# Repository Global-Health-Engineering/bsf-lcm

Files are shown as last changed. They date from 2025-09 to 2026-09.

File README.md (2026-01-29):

<!-- badges: start -->



<!-- badges: end -->

<h1> Black Soldier Fly Larvae Counting Machine </h1>

<b>Contributors</b>  
- Jonas Biner <a href="https://orcid.org/0009-0008-2161-3013">
ORCID logo 0009-0008-2161-3013
</a> *author, developer*  
- Jakub Tkaczuk <a href="https://orcid.org/0000-0001-7997-9423">
ORCID logo 0000-0001-7997-9423
</a> *supervisor, maintainer*  
- Christian Zurbrügg <a href="https://orcid.org/0000-0003-4980-4483">
ORCID logo 0000-0003-4980-4483
</a> *supervisor*  
- Stefan Diener <a href="https://orcid.org/0000-0002-6622-6980">
ORCID logo 0000-0002-6622-6980
</a> *supervisor*  
- Elizabeth Tilley <a href="https://orcid.org/0000-0002-2095-9724">
ORCID logo 0000-0002-2095-9724
</a> *supervisor*  

<br>
<p align="middle"> 

<br><br>
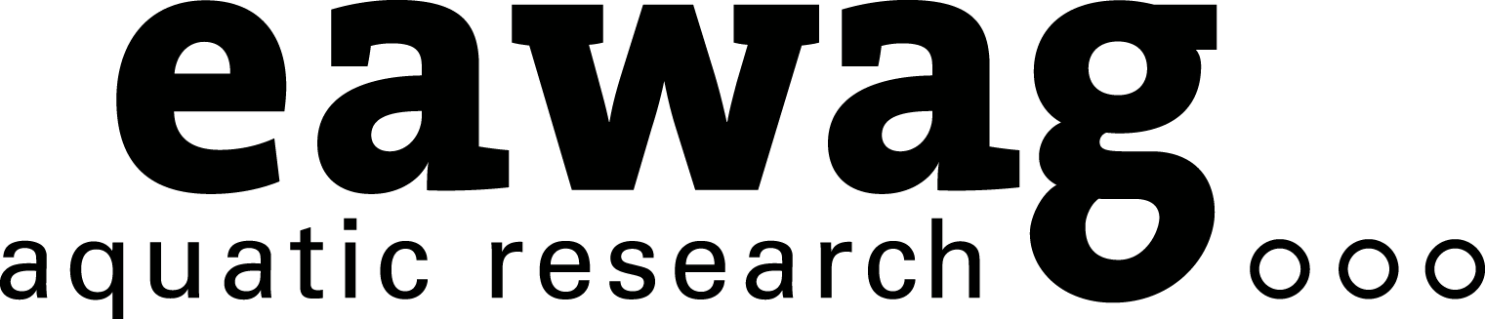
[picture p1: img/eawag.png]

<br><br>
<b>Complete description of system design, functionalities, and operation is available on  
<a href="https://global-health-engineering.github.io/bsf-lcm/">Github pages</a>  
</b>  
It compliments the openly-accessible master's thesis, available on the  
<a href="">ETH Research Collection</a>
</p>

# Overview

# Licenses

The three core elements of this project are licensed under:

| Component      | License                                                                                                |
|----------------|--------------------------------------------------------------------------------------------------------|
| Hardware       | [CERN-OHL-S 2.0](https://opensource.org/license/cern-ohl-s)                                            |
| Software       | [MIT](https://opensource.org/licenses/MIT)                                                             |
| Documentation  | [Creative Commons Attribution 4.0 International](https://creativecommons.org/licenses/by/4.0/)         |

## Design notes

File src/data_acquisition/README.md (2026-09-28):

# data-acquisition

'BSF_LCM_MK2.desktop' needs to be copied to '~/.config/autostart/' on Raspberry Pi for the program to start on boot.

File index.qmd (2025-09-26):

---
title: "Black Soldier Fly Larvae Counting Machine"
subtitle: "Design, Assembly, and Usage Manual"
number-sections: true
format: html
---

<!-- badges: start -->



<!-- badges: end -->

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

<br>
<p align="middle">
  
<br>
  
<br>
Github repository for this page sits [here](https://github.com/Global-Health-Engineering/bsf-lcm).
</p>

# Introduction {#sec-intro}

The Larvae Counting Machine (LCM) MK1 is designed to facilitate the counting of Five-Days-Old (5-DOL) Black Soldier Fly (BSF) larvae. It separates the larvae from frass and chicken feed to guarantee high homogeneity of the larvae batch making the sample more representative; and automates counting of samples. The process involves three steps:

- Sieving
- Sedimentation
- Counting

# Overview {#sec-overview}

The LCM MK1 consists of two funnels mounted on two flat boards and a 3D printed box containing the electronics. During operation the setup should look as shown in Figure 1.

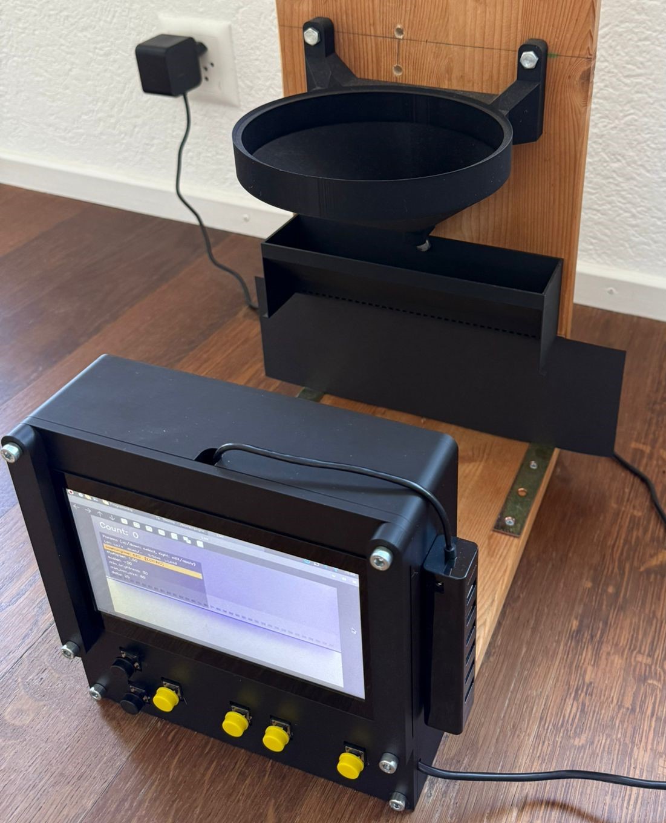
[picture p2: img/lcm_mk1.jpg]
Figure 1. Larvae Counting Machine Mark 1


The purpose of the first circular funnel is to facilitate the loading of larvae into the second funnel, which in turn forces them to spread out horizontally along the back wall and makes them fall out through holes on the side the funnel one after another. The falling larvae are filmed by a camera located at the back wall of the 3D printed electronics box. Then the LCM MK1 python program, running on a Raspberry Pi 5, uses frame differencing to count the larvae falling through the camera's field of view.

# Cost breakdown {#sec-costs}

# Licenses {#sec-license}

The three core elements of this project are licensed under:

| Component      | License                                                                                                |
|----------------|--------------------------------------------------------------------------------------------------------|
| Hardware       | [CERN-OHL-S 2.0](https://opensource.org/license/cern-ohl-s)                                            |
| Software       | [Apache 2.0](https://opensource.org/license/apache-2-0)                                                |
| Documentation  | [Creative Commons Attribution 4.0 International](https://creativecommons.org/licenses/by/4.0/)         |

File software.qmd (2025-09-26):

---
title: "Software"
number-sections: true
format: html
---

<!-- badges: start -->


<!-- badges: end -->

# Start up

To turn the larvae counting software on the Raspberry Pi 5:

- Plug in the power supply
- Wait until the Rapsberry Pi boots up
- Press and hold the **LCM Launch** icon, located on desktop
- Click **Open**
- Click **Execute**
- Double-click on the Top bar of the newly opened window to open it in a full screen mode

# Button Layout

The software allows the user to navigate the menu of the program with 6 built-in buttons. The function of each button is described in Figure 1.

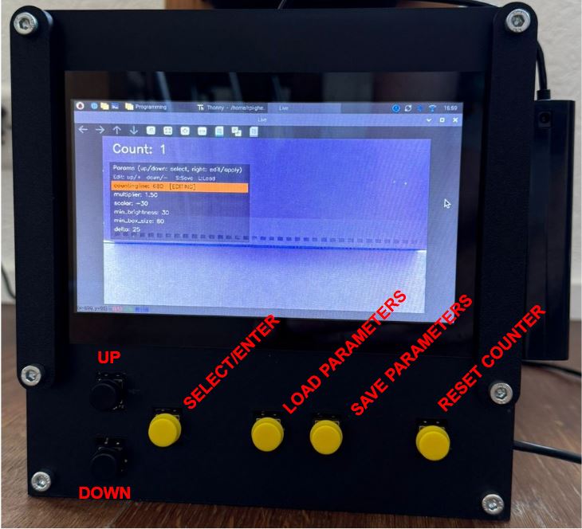
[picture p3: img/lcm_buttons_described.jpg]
Figure 1. Functional buttons


# Parameter Tuning

The constant parameters used by the software to differentiate and count the larvae can be tuned to adjust the system to the existing lighting conditions.

**Important**: All the images are converted into grey scale so each pixel has associated a single value ranging from 0 (black) to 255 (white).

The parameters used are as follows:

- **Multiplier** multiplies each pixel value of the taken images by a fixed value. It increases the contrast of the image but if the multiplied pixel value is 255 or higher, all pixes will be displayed as white.
- **Scalar**. This fixed number is added to each pixel value of the image so the the brightness of the black and white image can be changed.
- **Minimum brightness**. After the previous two transformations are applied to all pixes, the image is converted into a binary. Each pixel with value equal or higher than the minimum brightness is set to 255 (white) and all others are set to 0 (black).
- **Minimum box size** determines what minimum size in pixels a counted object, falling in front of the camera, should have. This parameter prevents counting of noise and chicken feed falling out of the funnel.
- **Delta** is used to prevent double counting of the same larvae by comparing the x coordinate of a larvae with the ones of previously counted larvae plus and minus the chosen delta value. Should a larvae have already been counted in the zone, the new box is not counted.
- **Counting line height**. In order to prevent the larvae from being counted while crawling around in the funnel, the program only counts the larvae below the counting line displayed in the live feed on the screen . The value should be set such that the line is always located right below the funnel, as shown in Figure 1.

The parameters should be set by default to make the machine operate according to expectations, so that only the **counting line height** should be adapted, if necessary. If frass particles smaller than the larvae are counted try increasing the **minimum box size**. If too many larvae are missed try decreasing the **minimum box size**.

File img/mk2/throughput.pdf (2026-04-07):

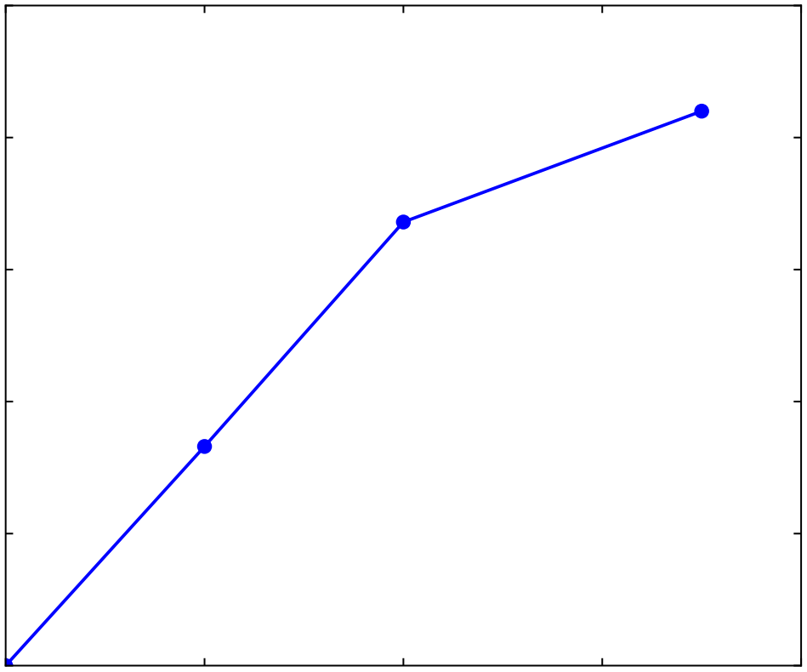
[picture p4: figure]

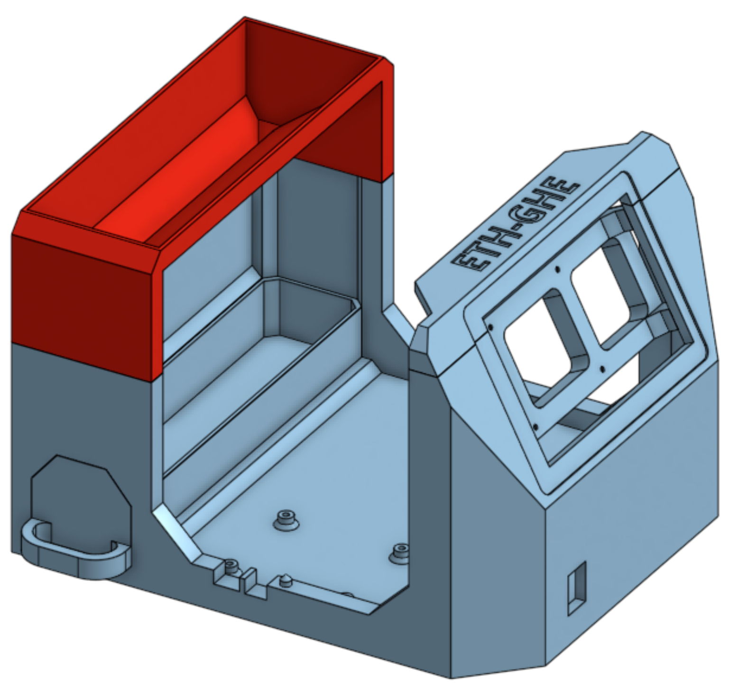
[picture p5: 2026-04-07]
img/mk2/divider_on_foundation_drawing.png

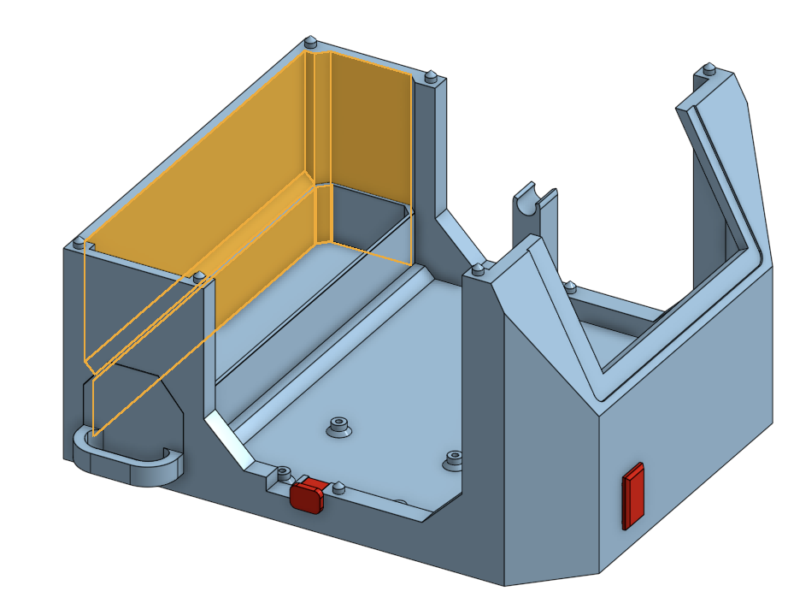
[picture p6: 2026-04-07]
img/mk2/painted_surface_right_view_drawing.png

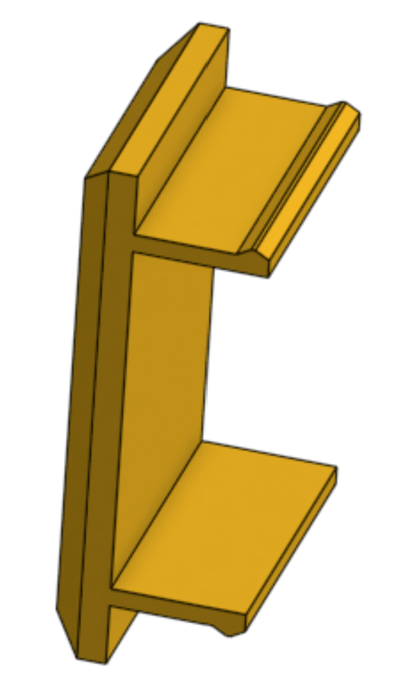
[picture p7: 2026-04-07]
img/mk2/cap_front_drawing.png

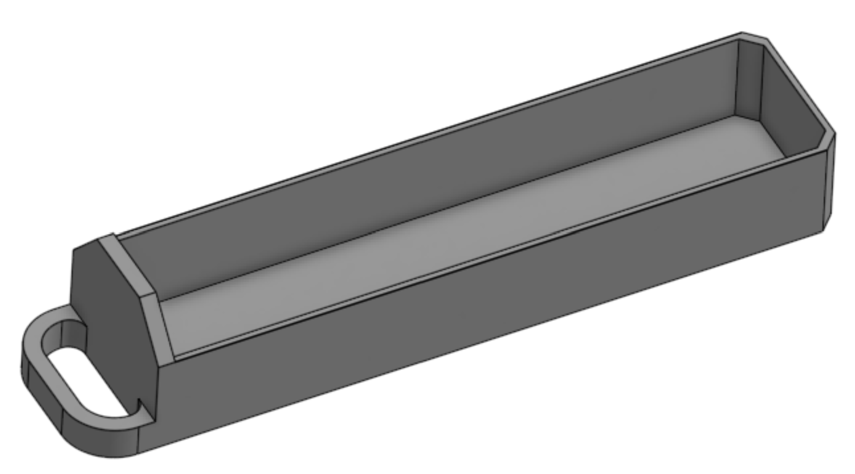
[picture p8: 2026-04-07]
img/mk2/collection_box_drawing.png

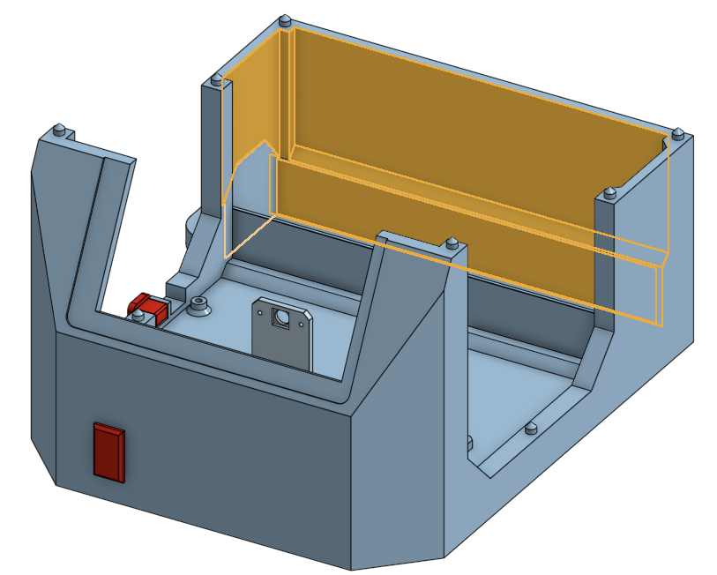
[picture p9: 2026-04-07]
img/mk2/painted_surface_left_view_drawing.png

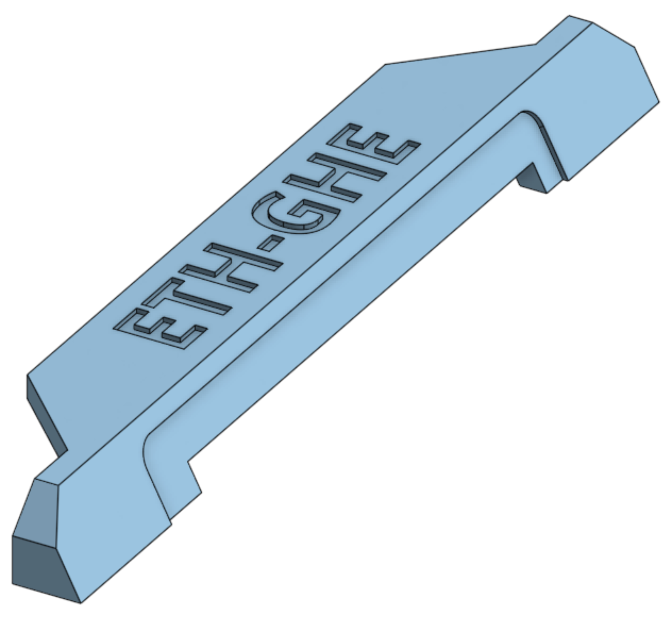
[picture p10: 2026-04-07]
img/mk2/top_part_drawing.png

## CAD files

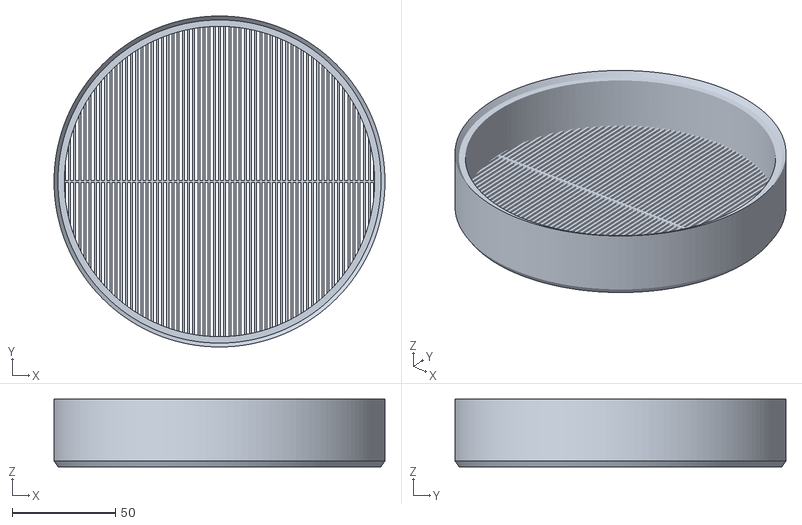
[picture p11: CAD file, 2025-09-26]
cad/mk1/150mm_sieve_1.5mm_1mm.stl
160.0 x 160.0 x 32.7

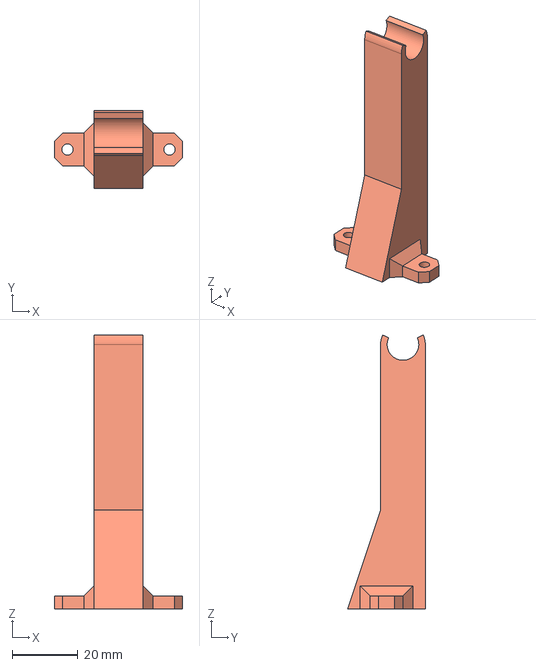
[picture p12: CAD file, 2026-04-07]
cad/mk2/counting/light_clamp.step
39.0 x 23.6 x 83.2 mm

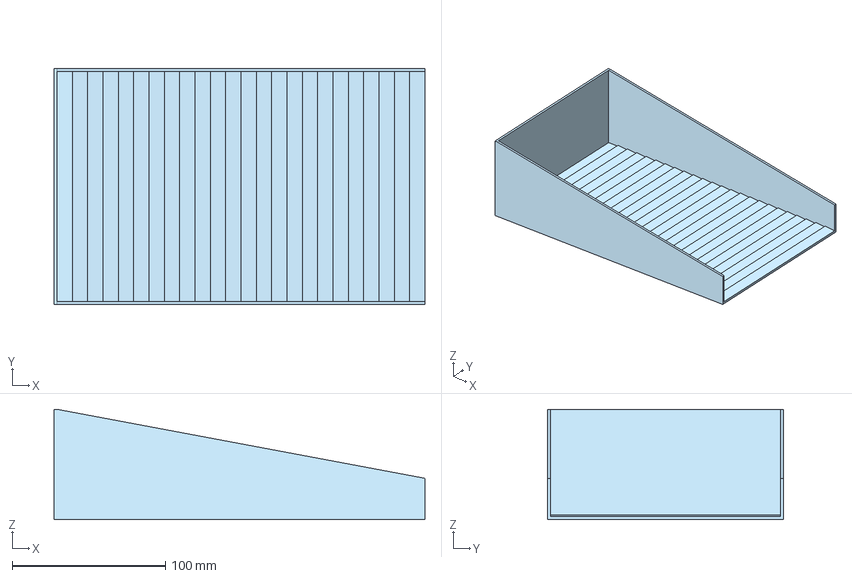
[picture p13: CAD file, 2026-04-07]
cad/mk2/separation/riffle_tray.step
242.0 x 154.0 x 72.0 mm

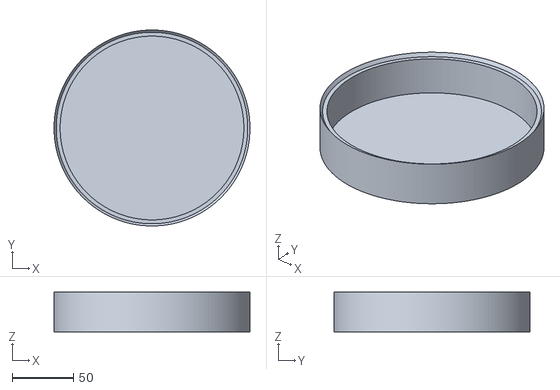
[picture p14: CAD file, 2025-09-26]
cad/mk1/150mm_collection_bowl.stl
160.0 x 160.0 x 32.6

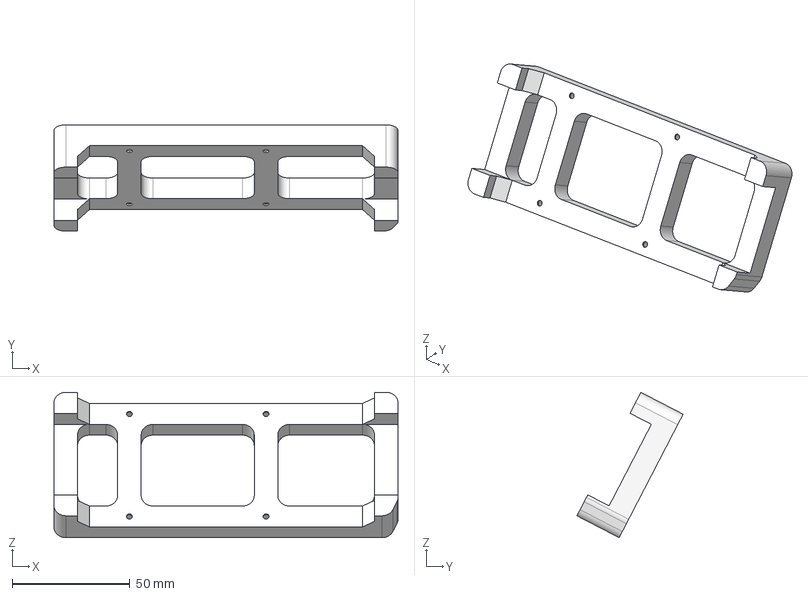
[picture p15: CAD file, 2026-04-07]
cad/mk2/counting/screen_clamp.step
146.0 x 45.1 x 61.7 mm

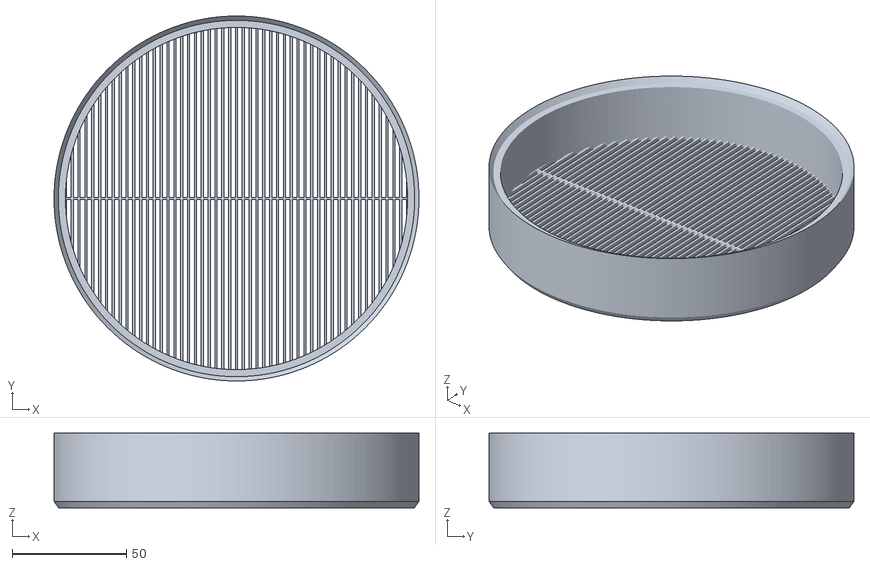
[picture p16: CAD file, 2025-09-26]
cad/mk2/separation/sieve_2mm_1mm.stl
160.0 x 160.0 x 32.7

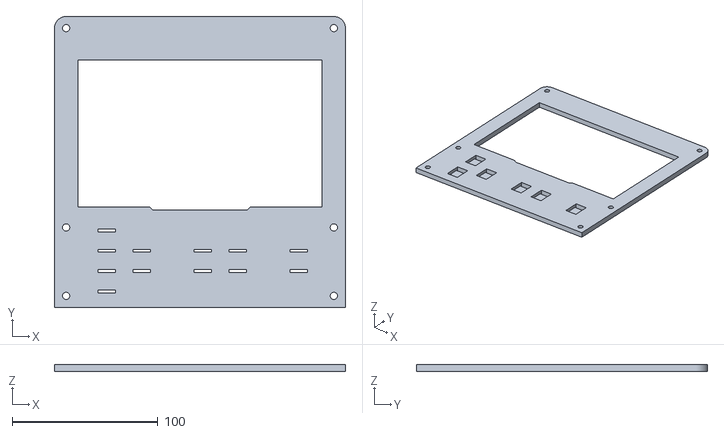
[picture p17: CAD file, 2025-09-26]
cad/mk1/lcm_front_plate.stl
200.0 x 200.0 x 5.00

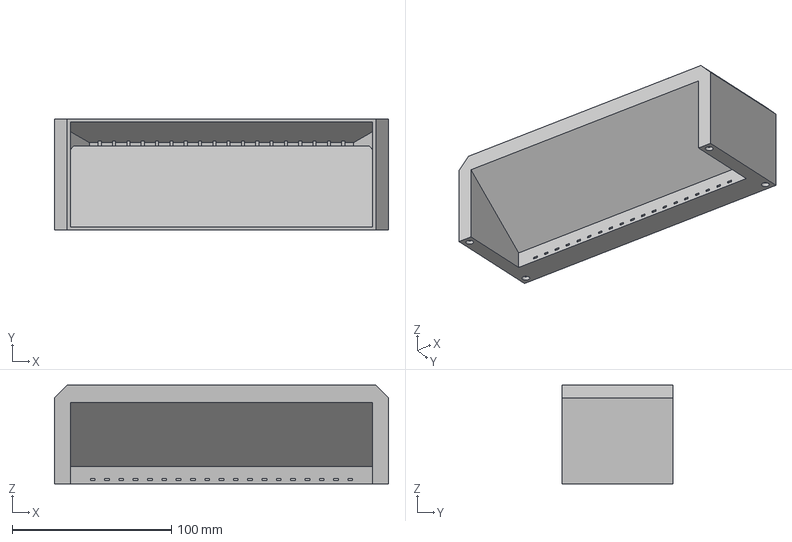
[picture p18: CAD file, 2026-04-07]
cad/mk2/counting/divider.step
210.0 x 70.0 x 62.0 mm

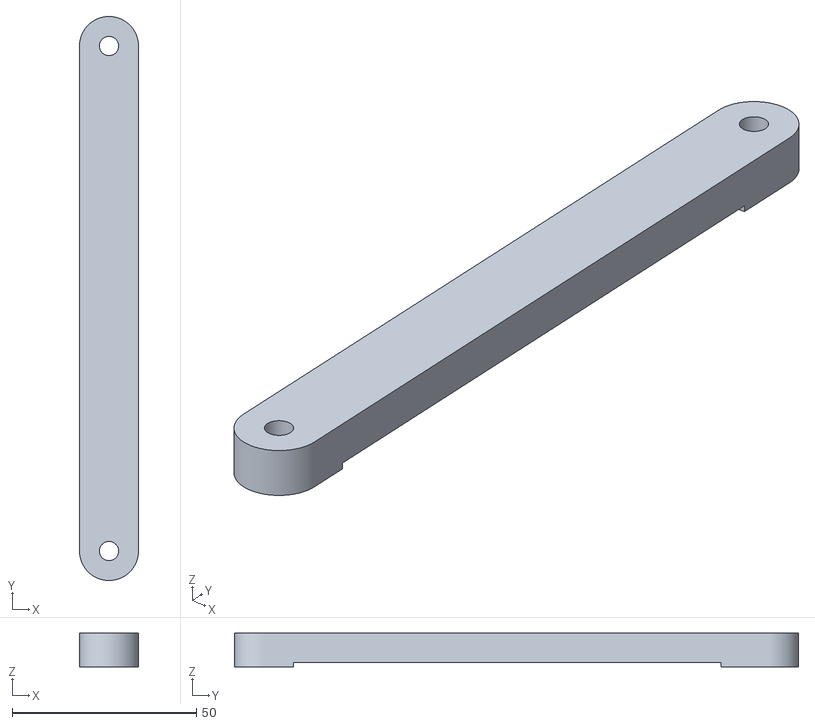
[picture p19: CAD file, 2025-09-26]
cad/mk1/lcm_screen_clamp.stl
16.0 x 153.0 x 9.20

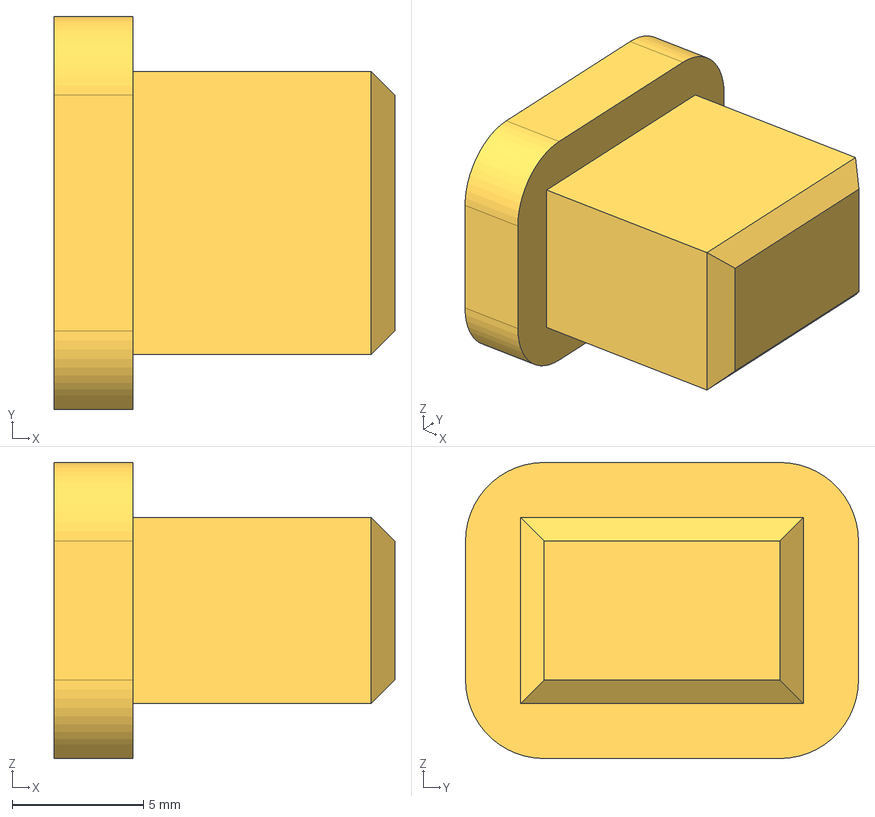
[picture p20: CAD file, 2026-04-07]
cad/mk2/counting/cap_left.step
13.0 x 15.0 x 11.3 mm

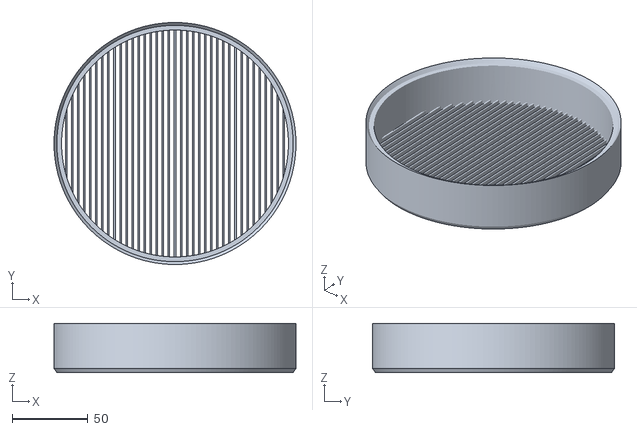
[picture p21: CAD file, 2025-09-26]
cad/mk1/150mm_sieve_3mm_1mm.stl
160.0 x 160.0 x 32.7

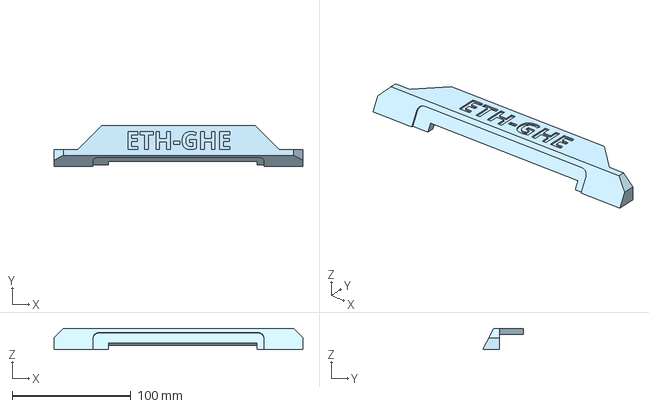
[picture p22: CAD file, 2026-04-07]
cad/mk2/counting/top_part.step
210.0 x 34.3 x 18.0 mm

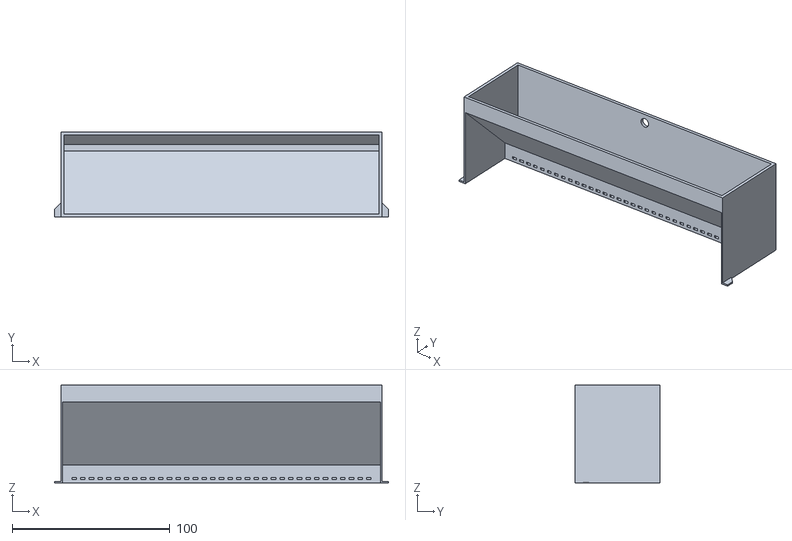
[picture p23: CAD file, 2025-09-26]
cad/mk1/collection_funnel_3x1.5mm.stl
212.0 x 54.0 x 62.0

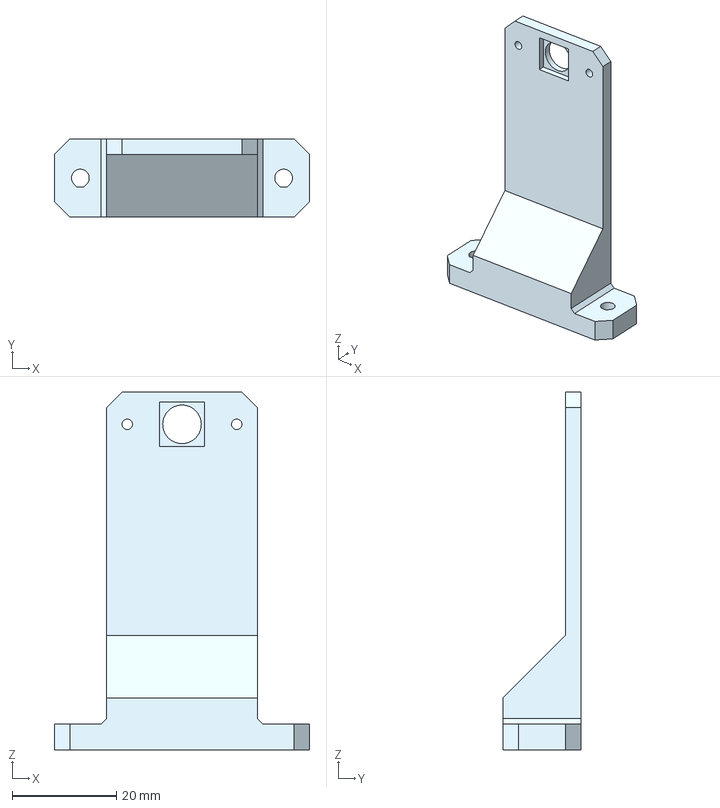
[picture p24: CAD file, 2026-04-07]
cad/mk2/counting/camera_mount.step
49.0 x 15.0 x 68.7 mm

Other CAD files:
cad/mk1/collection_box.stl
cad/mk1/150mm_funnel.stl
cad/mk1/lcm_box.stl
cad/mk1/lcm_cam_holder.stl
cad/mk2/counting/cap_front.step
cad/mk2/counting/collection_box.step
cad/mk2/counting/cover.step
cad/mk2/counting/foundation.step

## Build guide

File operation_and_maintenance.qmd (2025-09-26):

---
title: "Usage Manual"
number-sections: true
format: html
---

<!-- badges: start -->


<!-- badges: end -->

# Operation

Below, the the process of preparing and counting the 5-DOL with LCM MK1 is described. The entire batch of 5-DOL larvae should go through the sieving and the sedimentation step. This removes most of the chicken feed and frass from the larvae and removes larvae which are too small to be transferred and counted.

## Sieving

### Materials needed

- Sieves (3 mm, 2 mm, and 1.5 mm spacing)
- Collection bowl
- Two more containers (one for the larvae and one for the chicken feed)

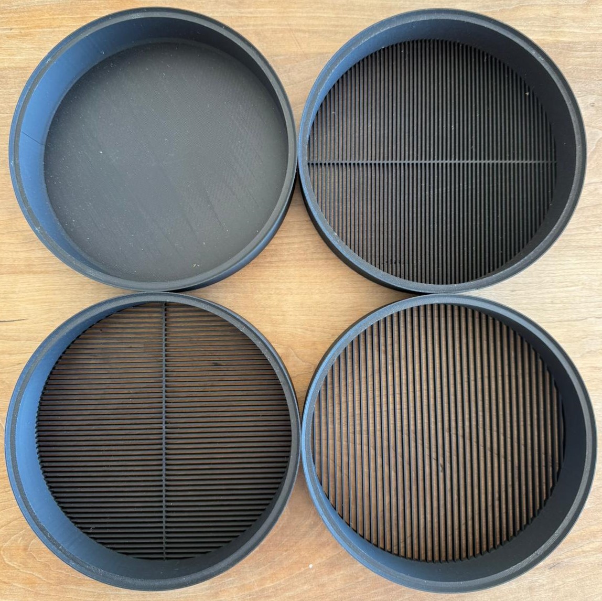
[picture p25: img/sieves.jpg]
Figure 1. Sieves


### Preparation

1. Place the collection bowl on the table.
2. Stack sieves on the bowl starting with the smallest gap on the bottom, progressing up to largest gap. Rotate each sieve 90° relative to sieve below. *(Only use 1.5 mm sieve if larvae are small enough to pass through it, otherwise they will get stuck).*

### Procedure

1. Pour **100 g of larvae mix** into the top sieve.
2. Remove the sieves one after another as soon as no more movement is spotted in the sieve (remove them carefully causing as little vibration as possible).
3. Pour the separated chicken feed from the removed sieves into chicken feed collection container.

Repeat the process if there are still large chunks of chicken feed visible in the larvae mix (2–3 times bigger than the size of the larvae).

**Important: Only process 100 g of larvae chicken feed mix per batch.**

## Sedimentation

The goal of the sedimentation step is to remove the frass from the previously sieved larvae. Additionally, by using the gold pan, larvae smaller than ~1 mm are also separated. To guarantee a high enough separation quality this step needs to be repeated multiple times.

### Materials needed

- Gold Pan  
- Container with sieved larvae (from the previous step)  
- 2 more containers (1 for processed larvae, 1 for frass to be dumped in)  

### Procedure

1. Hold the gold pan at an upward angle of around 45° and fill move the preprocessed larvae from the previous step into the gold pan (Processing 100 g of larvae and frass mix was successful; the maximum possible load must be found by trial and error), see Figure 2a.
2. Tilt the gold pan forward until larvae start pouring out into the collection container. Increase the angle steadily until all large larvae have fallen out of the pan, see Figures 2b and 2c.
3. Rotate the the gold pan back upwards to a steep angle and knock it on the back so the frass collects at the back side. Then knock from the side to move the frass into a corner. Pour the separated frass into the frass collection container *(Smaller larvae may remain in the frass and should be added back into the chicken feed larvae boxes for transfer and counting on a later day).*  

Repeat this three-step process until the amount of frass removed in each cycle decreases drastically. After finishing, pour the completely preprocessed larvae into another large collection container.  

::::{.columns}
::: {.column width="50%"}
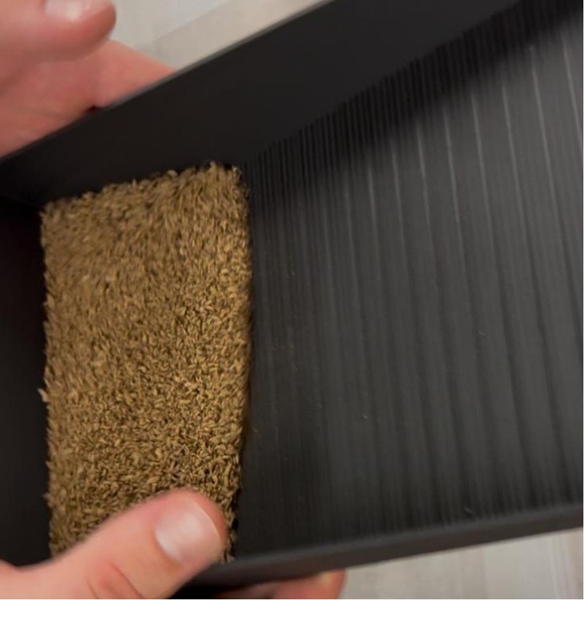
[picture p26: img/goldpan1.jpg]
Figure 2a. Fill the pan with larvae

:::

::: {.column width="50%"}
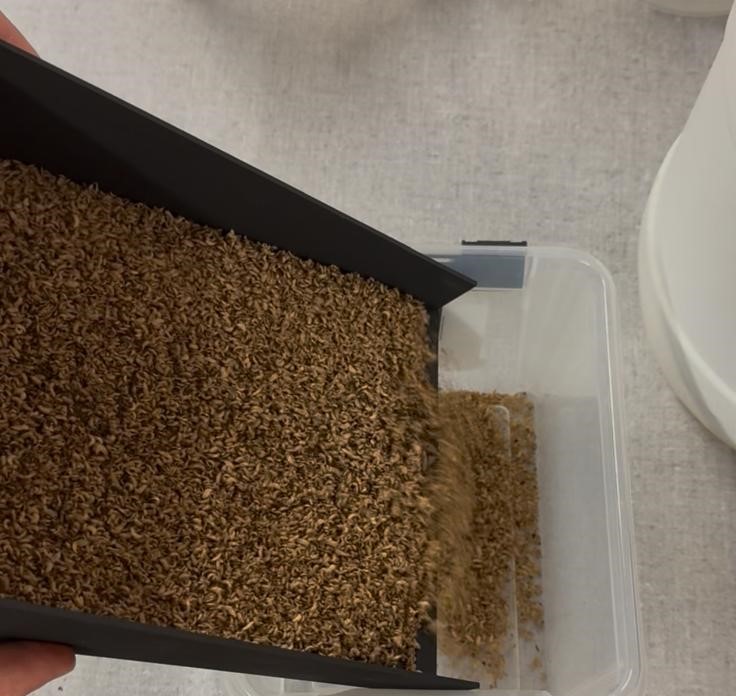
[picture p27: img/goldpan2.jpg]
Figure 2b. Tilt the pan forward slowly over a container

:::

::: {.column width="50%"}
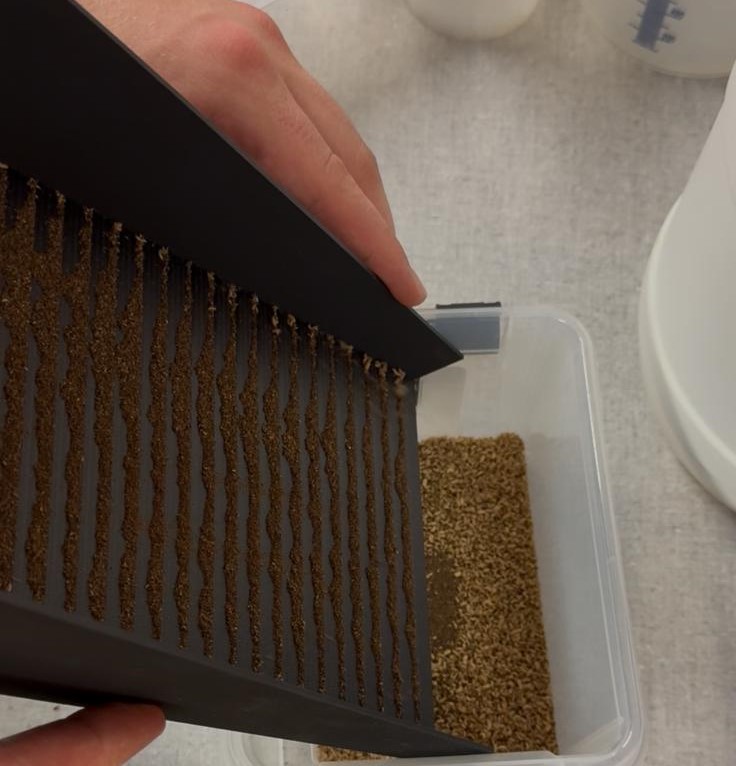
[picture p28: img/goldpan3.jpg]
Figure 2c. Let the larvae with some frass fall into the container

:::

::: {.column width="50%"}
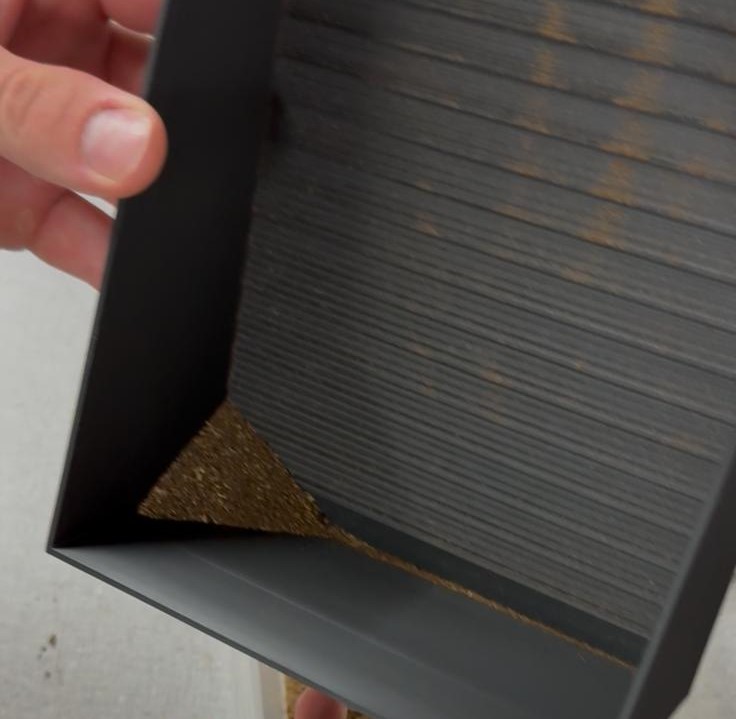
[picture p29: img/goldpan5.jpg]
Figure 2d. Tilt the pan backwards and knock the separated frass into a corner

:::
::::

## Counting

As soon as all the larvae have been preprocessed, they can be fed into the counting step.

Figure 3. Counting machine with running software

### Procedure

1. Take a sample from the freshly separated larvae.
2. Set the counter of the machine to 0 (click **RESET COUNTER**).
3. Pour the sample into the funnel of the counting machine.

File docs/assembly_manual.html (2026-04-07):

# Preparation and Assembly

 (https://opensource.org/license/cern-ohl-s)  (https://creativecommons.org/licenses/by/4.0/)

This project was supported by the Global Health Engineering Group at ETH Zurich (https://ghe.ethz.ch)

- (https://github.com/Global-Health-Engineering/bsf-lcm)
- (https://matrix.to/#/#ghe-open:staffchat.ethz.ch)

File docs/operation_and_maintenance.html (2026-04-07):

# Usage Manual

 (https://opensource.org/license/cern-ohl-s)  (https://creativecommons.org/licenses/by/4.0/)

# 1 Operation

Below, the the process of preparing and counting the 5-DOL with LCM MK1 is described. The entire batch of 5-DOL larvae should go through the sieving and the sedimentation step. This removes most of the chicken feed and frass from the larvae and removes larvae which are too small to be transferred and counted.

## 1.1 Sieving

### 1.1.1 Materials needed

- Sieves (3 mm, 2 mm, and 1.5 mm spacing)
- Collection bowl
- Two more containers (one for the larvae and one for the chicken feed)



Figure 1. Sieves

### 1.1.2 Preparation

1. Place the collection bowl on the table.
2. Stack sieves on the bowl starting with the smallest gap on the bottom, progressing up to largest gap. Rotate each sieve 90° relative to sieve below. (Only use 1.5 mm sieve if larvae are small enough to pass through it, otherwise they will get stuck).

### 1.1.3 Procedure

1. Pour 100 g of larvae mix into the top sieve.
2. Remove the sieves one after another as soon as no more movement is spotted in the sieve (remove them carefully causing as little vibration as possible).
3. Pour the separated chicken feed from the removed sieves into chicken feed collection container.

Repeat the process if there are still large chunks of chicken feed visible in the larvae mix (2–3 times bigger than the size of the larvae).

Important: Only process 100 g of larvae chicken feed mix per batch.

## 1.2 Sedimentation

The goal of the sedimentation step is to remove the frass from the previously sieved larvae. Additionally, by using the gold pan, larvae smaller than ~1 mm are also separated. To guarantee a high enough separation quality this step needs to be repeated multiple times.

### 1.2.1 Materials needed

- Gold Pan
- Container with sieved larvae (from the previous step)
- 2 more containers (1 for processed larvae, 1 for frass to be dumped in)

### 1.2.2 Procedure

1. Hold the gold pan at an upward angle of around 45° and fill move the preprocessed larvae from the previous step into the gold pan (Processing 100 g of larvae and frass mix was successful; the maximum possible load must be found by trial and error), see Figure 2a.
2. Tilt the gold pan forward until larvae start pouring out into the collection container. Increase the angle steadily until all large larvae have fallen out of the pan, see Figures 2b and 2c.
3. Rotate the the gold pan back upwards to a steep angle and knock it on the back so the frass collects at the back side. Then knock from the side to move the frass into a corner. Pour the separated frass into the frass collection container (Smaller larvae may remain in the frass and should be added back into the chicken feed larvae boxes for transfer and counting on a later day).

Repeat this three-step process until the amount of frass removed in each cycle decreases drastically. After finishing, pour the completely preprocessed larvae into another large collection container.



Figure 2a. Fill the pan with larvae



Figure 2b. Tilt the pan forward slowly over a container



Figure 2c. Let the larvae with some frass fall into the container



Figure 2d. Tilt the pan backwards and knock the separated frass into a corner

## 1.3 Counting

As soon as all the larvae have been preprocessed, they can be fed into the counting step.



Figure 3. Counting machine with running software

### 1.3.1 Procedure

1. Take a sample from the freshly separated larvae.
2. Set the counter of the machine to 0 (click RESET COUNTER).
3. Pour the sample into the funnel of the counting machine.

This project was supported by the Global Health Engineering Group at ETH Zurich (https://ghe.ethz.ch)

- (https://github.com/Global-Health-Engineering/bsf-lcm)
- (https://matrix.to/#/#ghe-open:staffchat.ethz.ch)

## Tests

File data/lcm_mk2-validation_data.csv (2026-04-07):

test_batch | manual_count | machine_count | diff | accuracy
1 | 97 | 100 | 3 | 0.969072165
2 | 117 | 120 | 3 | 0.974358974
3 | 127 | 130 | 3 | 0.976377953
4 | 177 | 197 | 20 | 0.88700565
5 | 73 | 70 | 3 | 0.95890411
6 | 77 | 83 | 6 | 0.922077922

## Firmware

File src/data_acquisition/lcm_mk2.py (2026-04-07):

import cv2
import numpy as np
import time
from picamera2 import Picamera2

# === Camera Setup ===
picam2 = Picamera2()
config = picam2.create_preview_configuration(main={"size": (3280, 1300), "format": "RGB888"})
picam2.configure(config)
picam2.start()
time.sleep(1)  # Allow camera to warm up

# === Parameters ===
counter = 0
countingline = 0.2
lowerlimit = 0.7

multiplier = 1
scalar = 0

min_brightness = 10
min_Area = 80
delta = 60

memory_current = []
memory_past = []

kernel = cv2.getStructuringElement(cv2.MORPH_RECT, (3, 3))

# === FPS CAP ===
TARGET_FPS = 16
FRAME_PERIOD = 1.0 / TARGET_FPS
# =================

# === LONG PRESS SETTINGS (reset counter) ===
LONG_PRESS_SECONDS = 0.8  # adjust (e.g. 0.5 .. 1.5)
press_start_time = None
press_active = False
# ==========================

# === EXIT BUTTON SETTINGS (black screen) ===
EXIT_HOLD_SECONDS = 1.2  # long-press EXIT for this many seconds to quit
exit_press_start = None
exit_press_active = False
exit_triggered = False
exit_btn = None  # (x1, y1, x2, y2)
# =========================================

# === DISPLAY MODE ===
maintenance = True  # True: show Live + Binary | False: show fullscreen black count screen
# ====================

# FPS shown on the black screen (updates once per second)
display_fps = 0

# === NO-COUNT WARNING SETTINGS ===
NO_COUNT_TIMEOUT_S = 120        # 2 minutes
FLASH_PERIOD_S = 1.0            # full on/off cycle duration (seconds)
BORDER_THICKNESS = 20
# ================================

# Track last time the counter increased
last_count_time = time.monotonic()

def point_in_rect(x, y, rect):
    x1, y1, x2, y2 = rect
    return (x1 <= x <= x2) and (y1 <= y <= y2)

# === Touch callback ===
def on_touch(event, x, y, flags, param):
    global press_start_time, press_active
    global exit_press_start, exit_press_active, exit_triggered
    global exit_btn

    if event == cv2.EVENT_LBUTTONDOWN:
        # If we're in black screen mode and the press is on EXIT button -> start exit hold
        if (not maintenance) and (exit_btn is not None) and point_in_rect(x, y, exit_btn):
            exit_press_start = time.monotonic()
            exit_press_active = True
        else:
            # Otherwise -> normal long-press reset
            press_start_time = time.monotonic()
            press_active = True

    elif event == cv2.EVENT_LBUTTONUP:
        # End both kinds of presses
        press_active = False
        press_start_time = None
        exit_press_active = False
        exit_press_start = None

# === Get First Frame ===
prev_frame = picam2.capture_array()
height, width = prev_frame.shape[:2]
prev_frame = cv2.convertScaleAbs(prev_frame, alpha=multiplier, beta=scalar)
prev_gray = cv2.cvtColor(prev_frame, cv2.COLOR_RGB2GRAY)

print(height, width)

prev_time = time.time()
frame_count = 0

countingline = round(countingline * height)
lowerlimit = round(lowerlimit * height)
calibration_area = 0

# Create windows + attach touch callback (touchscreen tap/press is mouse events)
if maintenance:
    cv2.namedWindow("Live")
    cv2.setMouseCallback("Live", on_touch)
    cv2.namedWindow("Binary")
else:
    cv2.namedWindow("Count", cv2.WINDOW_NORMAL)
    cv2.setMouseCallback("Count", on_touch)
    # Borderless fullscreen (where supported by your window manager)
    cv2.setWindowProperty("Count", cv2.WND_PROP_FULLSCREEN, cv2.WINDOW_FULLSCREEN)

try:
    while True:
        loop_start = time.perf_counter()  # === FPS CAP ===

        frame = picam2.capture_array()
        frame = cv2.convertScaleAbs(frame, alpha=multiplier, beta=scalar)
        gray = cv2.cvtColor(frame, cv2.COLOR_RGB2GRAY)

        # Frame differencing
        diff = cv2.subtract(gray, prev_gray)
        _, binary = cv2.threshold(diff, min_brightness, 255, cv2.THRESH_BINARY)
        binary = cv2.erode(binary, kernel, iterations=1)
        binary = cv2.dilate(binary, None, iterations=3)

        contours, _ = cv2.findContours(binary, cv2.RETR_EXTERNAL, cv2.CHAIN_APPROX_SIMPLE)

        # Only draw overlays on the frame when in maintenance mode
        if maintenance:
            cv2.drawContours(frame, contours, -1, (0, 255, 0), 3)

        for cnt in contours:
            area = cv2.contourArea(cnt)
            if area > calibration_area:
                calibration_area = area
                print(area)

            if area > min_Area:
                x, y, w, h = cv2.boundingRect(cnt)
                if maintenance:
                    cv2.rectangle(frame, (x, y), (x + w, y + h), (0, 0, 255), 2)
                cx = x + w // 2

                found = any(cx - delta <= val <= cx + delta for val in (memory_current + memory_past))
                if not found and (y + h) > countingline and y < lowerlimit:
                    counter += 1
                    last_count_time = time.monotonic()  # <-- mark last increment time
                    memory_current.append(cx)

        # === Long-press reset (checked in loop) ===
        if press_active and press_start_time is not None:
            held = time.monotonic() - press_start_time
            if held >= LONG_PRESS_SECONDS:
                counter = 0
                last_count_time = time.monotonic()
                print("Counter reset by long press")
                # Prevent repeated resets while still holding
                press_active = False
                press_start_time = None
        # =========================================

        # Optional: show reset hold progress
        hold_text = None
        if press_active and press_start_time is not None:
            held = time.monotonic() - press_start_time
            prog = min(held / LONG_PRESS_SECONDS, 1.0)
            hold_text = f"Hold to reset: {int(prog * 100)}%"

        # === Exit hold detection (only relevant in black screen) ===
        exit_hold_text = None
        if (not maintenance) and exit_press_active and exit_press_start is not None:
            held_exit = time.monotonic() - exit_press_start
            pct = int(min(held_exit / EXIT_HOLD_SECONDS, 1.0) * 100)
            exit_hold_text = f"Exiting: {pct}%"
            if held_exit >= EXIT_HOLD_SECONDS:
                exit_triggered = True
        # =========================================================

        if maintenance:
            # Draw horizontal counting line + UI
            cv2.line(frame, (0, countingline), (width, countingline), (255, 0, 0), 2)
            cv2.line(frame, (0, lowerlimit), (width, lowerlimit), (255, 0, 0), 2)
            cv2.line(frame, (0, 100), (2 * delta, 100), (255, 255, 0), 2)

            if hold_text is not None:
                cv2.putText(frame, hold_text, (30, 95),
                            cv2.FONT_HERSHEY_SIMPLEX, 0.8, (255, 255, 255), 2)

            cv2.putText(frame, f"Count: {counter}", (30, 50),
                        cv2.FONT_HERSHEY_SIMPLEX, 1.2, (255, 255, 255), 2)

            # Show previews
            preview = cv2.resize(frame, (960, 540))
            cv2.imshow("Live", preview)
            cv2.imshow("Binary", binary)

        else:
            # Fullscreen black screen (720x1280) with centered green count + FPS + warning border + EXIT button
            canvas_h, canvas_w = 720, 1280
            black = np.zeros((canvas_h, canvas_w, 3), dtype=np.uint8)

            # Define EXIT button rectangle (top-left)
            btn_w, btn_h = 220, 90
            btn_x1, btn_y1 = 20, 20
            btn_x2, btn_y2 = btn_x1 + btn_w, btn_y1 + btn_h
            exit_btn = (btn_x1, btn_y1, btn_x2, btn_y2)

            # Draw EXIT button (red)
            cv2.rectangle(black, (btn_x1, btn_y1), (btn_x2, btn_y2), (0, 0, 255), -1)
            cv2.putText(black, "EXIT", (btn_x1 + 45, btn_y1 + 62),
                        cv2.FONT_HERSHEY_SIMPLEX, 1.6, (255, 255, 255), 3)

            # === Inactivity flashing border (blue if count=0, red otherwise) ===
            inactive_for = time.monotonic() - last_count_time
            if inactive_for >= NO_COUNT_TIMEOUT_S:
                phase = (time.monotonic() % FLASH_PERIOD_S) < (FLASH_PERIOD_S / 2.0)
                if phase:
                    # Green if counter is zero, otherwise red
                    border_color = (0, 255, 0) if counter == 0 else (0, 0, 255)

                    cv2.rectangle(
                        black,
                        (0, 0),
                        (canvas_w - 1, canvas_h - 1),
                        border_color,
                        BORDER_THICKNESS
                    )
            # ================================================================


            # Centered count
            text = str(counter)
            font = cv2.FONT_HERSHEY_SIMPLEX
            font_scale = 4.0
            thickness = 6
            color = (0, 255, 0)  # Green (BGR)

            (text_w, text_h), _ = cv2.getTextSize(text, font, font_scale, thickness)
            x = (canvas_w - text_w) // 2
            y = (canvas_h + text_h) // 2
            cv2.putText(black, text, (x, y), font, font_scale, color, thickness)

            # Optional: show reset hold progress below count
            if hold_text is not None:
                cv2.putText(black, hold_text, (x, y + 80),
                            cv2.FONT_HERSHEY_SIMPLEX, 1.0, (0, 255, 0), 2)

            # Show exit hold progress under the EXIT button
            if exit_hold_text is not None:
                cv2.putText(black, exit_hold_text, (btn_x1, btn_y2 + 35),
                            cv2.FONT_HERSHEY_SIMPLEX, 0.9, (0, 0, 255), 2)

            # FPS at top-right
            fps_text = f"FPS: {display_fps}"
            fps_scale = 1.0
            fps_thickness = 2
            (fps_w, fps_h), _ = cv2.getTextSize(fps_text, font, fps_scale, fps_thickness)
            fps_x = canvas_w - fps_w - 20
            fps_y = fps_h + 20
            cv2.putText(black, fps_text, (fps_x, fps_y),
                        font, fps_scale, (0, 255, 0), fps_thickness)

            cv2.imshow("Count", black)

        prev_gray = gray.copy()
        memory_past = memory_current
        memory_current = []

        frame_count += 1
        current_time = time.time()

        if current_time - prev_time >= 1.0:
            display_fps = frame_count
            print("FPS:", display_fps)
            print("Noise:", calibration_area)
            frame_count = 0
            prev_time = current_time

        # Exit button long-press triggers quit
        if exit_triggered:
            break

        # Press q to quit (if a keyboard is attached)
        if cv2.waitKey(1) & 0xFF == ord('q'):
            break

        # === FPS CAP ===
        elapsed = time.perf_counter() - loop_start
        sleep_time = FRAME_PERIOD - elapsed
        if sleep_time > 0:
            time.sleep(sleep_time)
        # =================

finally:
    picam2.stop()
    cv2.destroyAllWindows()

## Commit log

2025-09-26 make github pages
    [150mm_collection_bowl.stl, 150mm_funnel.stl, 150mm_sieve_1.5mm_1mm.stl, 150mm_sieve_2mm_1mm.stl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]
2026-04-07 cleanup cad drawings
    [150mm_collection_bowl.stl, 150mm_funnel.stl, 150mm_sieve_1.5mm_1mm.stl, 150mm_sieve_2mm_1mm.stl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]
2026-04-07 add val data
    [lcm_mk2-throughput.csv, lcm_mk2-validation_data.csv]
2026-04-09 simplify names
    [camera_mount.step, cap_front.step, cap_left.step, collection_box.step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]

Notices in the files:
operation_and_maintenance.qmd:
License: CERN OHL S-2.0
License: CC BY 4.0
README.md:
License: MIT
